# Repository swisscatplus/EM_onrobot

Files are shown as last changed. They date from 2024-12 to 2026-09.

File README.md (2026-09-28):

<br />
<div align="center">
  <a href="https://github.com/swisscatplus/EM_onrobot">
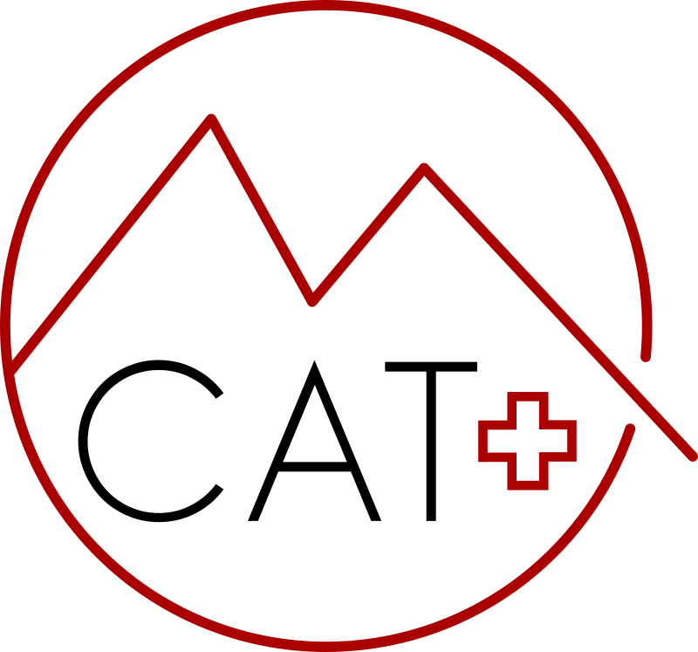
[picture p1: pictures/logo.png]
    
  </a>
  <h1 align="center">EM_onrobot</h1>
</div>

This is the software that runs **on the mobile robot** (on its Raspberry Pi). It:

- drives the two wheels from velocity commands (`cmd_vel`)
- measures how far the wheels turned (wheel odometry)
- reads the BNO055 IMU (orientation and acceleration sensor)
- finds the robot's position on the lab map with the camera and ArUco markers
- merges all of that into one position estimate (EKF, `robot_localization`)
- reports the robot's health (diagnostics)

Path planning, path following and fleet management are **not** here: they live in [EM_fleetmanager](https://github.com/swisscatplus/EM_fleetmanager), which runs on a laptop and sends commands to the robot.

> [!WARNING]
> **Protect the SD card.** The Raspberry Pi runs from an SD card, and SD cards wear out quickly when they are written to all the time. Several robots have already lost their card this way. Please:
>
> - Run `sudo ./scripts/setup_pi_sd_protection.sh` once on every new robot (see [step 6](#6-protect-the-sd-card)).
> - **Do not** record ROS bags (`ros2 bag record`), images or other large files on the robot's SD card. Record them on your laptop, or on a USB stick plugged into the robot.
> - **Do not** add `colcon build` to the container's start command, and do not change `--restart unless-stopped` in `deploy_dev.sh`. Both are set up on purpose (see [How it starts](#how-the-robot-starts-by-itself)).
> - Do not add log messages that print many times per second. If a message runs inside a loop or timer, throttle it: `self.get_logger().warn("...", throttle_duration_sec=2.0)`.
> - When you can, shut down cleanly (`sudo shutdown now`) before cutting the battery. Cutting the power while the card is being written can corrupt it.
>
> Buy "High Endurance" SD cards (for example Samsung PRO Endurance or SanDisk High Endurance) for the robots.

## Contents

1. [Words you need to know](#words-you-need-to-know)
2. [How the robot starts by itself](#how-the-robot-starts-by-itself)
3. [First-time setup of a new robot](#first-time-setup-of-a-new-robot)
4. [Everyday use](#everyday-use)
5. [Updating the code on the robot](#updating-the-code-on-the-robot)
6. [Talking to the robot from your laptop](#talking-to-the-robot-from-your-laptop)
7. [Troubleshooting](#troubleshooting)
8. [Advanced topics](#advanced-topics)

## Words you need to know

| Word | What it means here |
|---|---|
| **ROS 2** | The framework the robot software is built with. We use the **Humble** version. |
| **Node** | One small program, for example `base_controller`, which drives the wheels. The robot runs about ten nodes at the same time. |
| **Topic** | A named channel that nodes use to send each other messages, for example `/robot1/cmd_vel` (speed commands) or `/robot1/odomWheel` (wheel odometry). |
| **Namespace** | A prefix in front of every topic, such as `robot1`, so that several robots can share the same network without mixing up their topics. |
| **ROS_DOMAIN_ID** | A number that decides which machines can see each other's topics. The robot uses **10**. Your laptop must use 10 too. |
| **Launch file** | A file that starts several nodes at once. Here: `bringup.launch.py`. |
| **Docker image** | A frozen, ready-to-use copy of an operating system with ROS and all libraries installed. |
| **Docker container** | A running instance of an image. The robot software runs inside a container called `em_robot_dev`. |
| **colcon build** | The command that compiles the ROS code. It creates the `build/` and `install/` folders. |

## How the robot starts by itself

```text
Robot powers on
  └─ Raspberry Pi boots
      └─ Docker starts
          └─ Docker restarts the container "em_robot_dev" (because of --restart unless-stopped)
              └─ the container runs: ros2 launch em_robot bringup.launch.py
                  └─ all the nodes start: wheels, IMU, camera, localization, EKF, diagnostics
```

You do **not** need to start anything by hand after a power cycle, for example after charging the battery. Wait about one minute after power-on, and the robot is ready.

The code is compiled **only** when you run `./scripts/deploy_dev.sh`, never at start-up. This keeps start-up fast and saves the SD card.

## First-time setup of a new robot

Do this once per robot. Every step ends with a check: do not go to the next step until the check passes.

You need:

- the robot with its Raspberry Pi, camera, BNO055 IMU, U2D2 adapter and the two Dynamixel motors
- a charged battery (the U2D2 does **not** power the motors: the motors need the battery)
- a laptop on the same Wi-Fi network as the robot
- an internet connection for the robot during setup (to download the Docker image)

### 1. Connect to the Raspberry Pi

From your laptop, connect over SSH. Replace `<user>` and `<robot-ip>` with the robot's values (ask your supervisor):

```bash
ssh <user>@<robot-ip>
```

All the commands below run **on the robot**, in this SSH session, unless a step says otherwise.

**Check:** your terminal prompt now shows the robot's name.

### 2. Install Docker

```bash
curl -fsSL https://get.docker.com | sudo sh
sudo usermod -aG docker $USER
```

Log out (`exit`) and SSH in again so the group change applies.

**Check:** `docker run --rm hello-world` prints "Hello from Docker!".

### 3. Download this repository

```bash
cd ~
git clone https://github.com/swisscatplus/EM_onrobot.git
cd EM_onrobot
```

From now on, run every command from this `~/EM_onrobot` folder.

### 4. Give the robot its name

Every robot needs its own namespace (`robot1`, `robot2`, ...), otherwise two robots on the same network would mix their topics.

```bash
cp config/robot.local.env.example config/robot.local.env
nano config/robot.local.env
```

Set `ROBOT_NAMESPACE=robot1` (or `robot2`, ... if other robots already use `robot1`). Save with `Ctrl+O`, `Enter`, then quit with `Ctrl+X`.

This file is ignored by Git, so `git pull` never overwrites it.

**Check:** `cat config/robot.local.env` shows your namespace.

### 5. Set up the hardware access

**a. Motors: give the U2D2 a fixed name.** Linux names USB adapters `/dev/ttyUSB0`, `/dev/ttyUSB1`, ..., and the number can change at every reboot. We create a rule so the U2D2 is always called `/dev/dynamixel`.

First, plug in the U2D2 and find its IDs:

```bash
lsusb | grep -i 0403
```

You should see something like `ID 0403:6001 Future Technology Devices ...`. The part after `0403:` is the product ID (here `6001`). If yours is different, for example `6014`, use your value in `idProduct` below.

Create the rule:

```bash
sudo tee /etc/udev/rules.d/99-dynamixel.rules > /dev/null <<'EOF'
# Match the FTDI chip of the Dynamixel U2D2
SUBSYSTEM=="tty", ATTRS{idVendor}=="0403", ATTRS{idProduct}=="6001", SYMLINK+="dynamixel", MODE="0666", GROUP="dialout"
EOF
sudo udevadm control --reload-rules
sudo udevadm trigger
```

**Check:** `ls -l /dev/dynamixel` shows `/dev/dynamixel -> ttyUSB0` (the number may differ).

If another FTDI adapter is plugged into the robot, the rule can pick the wrong one. In that case, add `ATTRS{serial}=="<serial>"` to the rule, using the U2D2 serial number shown by `udevadm info -a -n /dev/ttyUSB0 | grep serial`.

**b. IMU: enable I2C.** The BNO055 is connected over I2C.

```bash
sudo raspi-config
```

Go to **Interface Options → I2C → Yes**, then reboot (`sudo reboot`).

**Check:** `ls /dev/i2c-1` exists, and `sudo i2cdetect -y 1` shows `28` in the table (the IMU's address).

**c. Camera.** **Check:** `ls /dev/video0` exists.

### 6. Protect the SD card

```bash
sudo ./scripts/setup_pi_sd_protection.sh
sudo reboot
```

This script:

- stops Linux from writing on every file read (`noatime`)
- keeps the system logs in RAM instead of on the card (they are lost at each reboot)
- turns off swap on the SD card
- limits the size of Docker logs

It backs up every file it changes (`<file>.bak.<date>`). You can run it again safely.

**Check:** after the reboot, `swapon --show` prints nothing.

### 7. Allow the robot to download the Docker image

The robot's Docker image (`ghcr.io/swisscatplus/em_onrobot/em_robot_base`) is stored on GitHub. If it is private, log in once with a GitHub account that has access. Create a token at GitHub → Settings → Developer settings → Personal access tokens, with the `read:packages` permission, then run:

```bash
docker login ghcr.io -u <your-github-username>
```

Paste the token when it asks for a password.

### 8. Deploy

Make sure the battery is connected (the motors must be powered), then:

```bash
./scripts/deploy_dev.sh
```

The first time, this downloads a large image (several GB) and can take a while. The script:

1. compiles the code once (`colcon build`)
2. stops the old container, if there is one
3. starts the `em_robot_dev` container, which launches all the nodes

**Check:** follow [Is the robot running?](#is-the-robot-running) below.

Finally, reboot the robot (`sudo reboot`) and check again: this confirms that it starts by itself.

## Everyday use

### Power on

Connect the battery and wait about one minute. Everything starts by itself.

### Is the robot running?

On the robot (over SSH):

```bash
docker ps
```

You should see `em_robot_dev` with the status `Up ...`.

- `Restarting` means that a node crashes at start-up. Read the logs, see [Troubleshooting](#troubleshooting).
- If `em_robot_dev` is missing, run `./scripts/deploy_dev.sh`.

Read the logs (`Ctrl+C` to stop reading; this does not stop the robot):

```bash
docker logs -f --tail 100 em_robot_dev
```

List the topics from inside the container:

```bash
docker exec -it em_robot_dev bash
source /opt/ros/humble/setup.bash
source /ros2_ws/install/setup.bash
ros2 topic list
```

You should see topics such as `/robot1/cmd_vel`, `/robot1/odomWheel`, `/robot1/bno055/imu` and `/robot1/odometry/filtered`. Type `exit` to leave the container.

### Useful topics

(Replace `robot1` with your robot's namespace.)

| Topic | What it contains |
|---|---|
| `/robot1/cmd_vel` | Speed commands **to** the robot (linear speed in m/s, rotation speed in rad/s) |
| `/robot1/odomWheel` | Position estimated from the wheels only |
| `/robot1/bno055/imu` | IMU data |
| `/robot1/odometry/filtered` | Best position estimate (wheels + IMU, fused by the EKF) |
| `/tf` | Positions of all the frames (`map`, `robot1/odom`, `robot1/base_link`, ...) |

See how often a topic publishes: `ros2 topic hz /robot1/odomWheel`. Print its messages: `ros2 topic echo /robot1/odomWheel`.

### Make the robot move (test)

> [!CAUTION]
> The robot will move. Put it on the floor with free space around it, or lift it so the wheels do not touch anything.

Inside the container (see above), send a slow forward command 10 times per second:

```bash
ros2 topic pub -r 10 /robot1/cmd_vel geometry_msgs/msg/Twist "{linear: {x: 0.05}, angular: {z: 0.0}}"
```

Press `Ctrl+C` to stop sending. The robot stops by itself about one second after the last command (safety watchdog).

To send the robot along a path, use [EM_fleetmanager](https://github.com/swisscatplus/EM_fleetmanager) from your laptop.

### Power off

When you can, shut down cleanly before cutting the battery:

```bash
sudo shutdown now
```

Wait until the Raspberry Pi's green LED stops blinking, then disconnect the battery.

## Updating the code on the robot

After new code was pushed to GitHub, on the robot:

```bash
cd ~/EM_onrobot
git pull
./scripts/deploy_dev.sh
```

Changed a file directly on the robot?

| What you changed | What to run |
|---|---|
| An existing Python file (`.py`) or config file (`.yaml`) | `docker restart em_robot_dev` is enough |
| Added a new file, node, message or service, or changed `setup.py` / `package.xml` | `./scripts/deploy_dev.sh` (recompiles) |
| Not sure | `./scripts/deploy_dev.sh`: it is always safe |

`docker restart` does **not** recompile. If the compilation fails, `deploy_dev.sh` stops and the robot keeps running the previous version.

## Talking to the robot from your laptop

Your laptop can see the robot's topics and send it commands, if:

1. **Both are on the same network**: the robot's Wi-Fi router.
2. **Your laptop has no other network active.** If your laptop is also plugged into another network (for example a network cable), ROS may send its discovery messages there and never find the robot. Unplug the cable, or run `nmcli dev disconnect eth0`.
3. **Your laptop uses the same domain**: `export ROS_DOMAIN_ID=10`. Put this line in your `~/.bashrc` so you do not forget it.
4. **Your laptop uses ROS 2 Humble**, like the robot. Other versions (for example Jazzy) can often list the topics, but may fail to read some messages. The simplest way to get Humble on any Linux laptop is the laptop Docker setup of EM_fleetmanager.

Then, on your laptop:

```bash
ros2 daemon stop    # forget old discovery results
ros2 topic list
```

**Check:** you see the `/robot1/...` topics.

If you do not see them:

- Check that your laptop can reach the robot: `ping <robot-ip>`.
- Check that ROS discovery can get through the network. Run `ros2 multicast receive` on your laptop, then `ros2 multicast send` on the robot, inside the container. If nothing arrives, the network or a firewall blocks discovery (`sudo ufw status`).

## Troubleshooting

First, always read the logs: `docker logs --tail 100 em_robot_dev`. Then find your error below.

| What you see | Most likely cause | What to do |
|---|---|---|
| `Failed to open Dynamixel port: /dev/dynamixel` | The U2D2 is not plugged in, or the udev rule is missing | Check `ls -l /dev/dynamixel`, and redo [step 5a](#5-set-up-the-hardware-access) |
| `Profile acceleration setup failed on motor ID=2` or `Torque enable failed on motor ID=...` | The robot can open the U2D2 but the motors do not answer. Usually the motors are not powered (battery flat or disconnected). It can also be a loose motor cable, or a motor whose ID or baud rate was changed. | Check the battery and the cables. At power-on, the LEDs on the motors should blink once. The motors must use IDs 1 (left) and 2 (right) at 57600 baud, which you can check with Dynamixel Wizard 2.0 on a laptop. |
| `Failed to read present position for motor ID=...` while running | The motor connection is lost | Check the battery level and the motor cables |
| IMU errors (`Receiving sensor data failed`, ...) | I2C is disabled or the IMU is badly connected | Redo [step 5b](#5-set-up-the-hardware-access). `sudo i2cdetect -y 1` must show `28`. |
| `docker ps` shows `Restarting` | A node crashes at start-up | Read the logs to find which one, then look for its error in this table |
| `Registry pull failed` or `unauthorized` | You are not logged in to GitHub's registry | Redo [step 7](#7-allow-the-robot-to-download-the-docker-image) |
| `lookup registry-1.docker.io ... server misbehaving` or `Temporary failure in name resolution` | The robot has no internet | Connect the robot to a network with internet access to download the image |
| The topics show on the robot but not on the laptop | Network or configuration problem | See [Talking to the robot from your laptop](#talking-to-the-robot-from-your-laptop) |
| The robot does not start after a reboot | The container was removed, or Docker does not start at boot | `sudo systemctl enable docker`, then `./scripts/deploy_dev.sh` |

Still stuck? Copy the last 100 lines of the logs (`docker logs --tail 100 em_robot_dev`) and send them to your supervisor.

## Advanced topics

The sections below are for maintainers. You do not need them to deploy and use the robot.

### Runtime profiles

A profile is a YAML file that decides which nodes start and with which settings. Profile files live in [`src/em_robot/config/profiles`](./src/em_robot/config/profiles).

| Profile | Intended system | Movement | IMU | Camera | Purpose |
|---|---|---|---|---|---|
| `real_robot` (default) | Raspberry Pi on robot | real Dynamixel base | BNO055 | Picamera2 | Production robot runtime |
| `work_ubuntu_localization_test` | Ubuntu workstation | disabled | disabled | OpenCV camera | Desktop validation of marker localization |

`deploy_dev.sh` uses `real_robot` unless you set `EM_ROBOT_PROFILE_VALUE` in `config/robot.local.env`. The container runs:

```bash
ros2 launch em_robot bringup.launch.py profile:=real_robot namespace:=robot1
```

The runtime URDF used by `robot_state_publisher` is packaged with `em_robot` at [`src/em_robot/urdf/simple_box_robot.urdf`](./src/em_robot/urdf/simple_box_robot.urdf). Hardware design files are intentionally kept outside this software repository.

### What `deploy_dev.sh` does

1. Loads `config/robot.local.env` (namespace, profile).
2. Picks the base image: the local `em_robot_base:local` if it exists, otherwise it pulls `ghcr.io/swisscatplus/em_onrobot/em_robot_base:latest`. `ALLOW_LOCAL_BASE_BUILD=1` builds it on the robot if the pull fails (this takes a very long time on a Raspberry Pi).
3. Runs `colcon build --symlink-install` once, in a throwaway container. The workspace is bind-mounted, so `build/` and `install/` are written to the repository folder. colcon's own logs are discarded.
4. Replaces the `em_robot_dev` container. That container only runs `ros2 launch`, with:
   - `--restart unless-stopped`, which restarts it at boot. Do not use `on-failure`: Docker does not restart those containers at boot.
   - Docker logs capped at 2 × 10 MB
   - `/root/.ros/log` and `/tmp` in RAM (tmpfs)
   - host networking, so ROS discovery works on the robot's network
   - access to `/dev` (motors, camera, I2C)

### Ubuntu validation

Use this when validating localization with a USB camera on an Ubuntu workstation:

```bash
export EM_ROBOT_CAMERA_DEVICE=/dev/video0
./scripts/start_dev.sh work_ubuntu_localization_test
```

Stop it with:

```bash
./scripts/start_dev.sh work_ubuntu_localization_test down
```

The validation profile uses:

- calibration from [`src/em_robot/config/calibration_ubuntu_test.yaml`](./src/em_robot/config/calibration_ubuntu_test.yaml)
- marker map from [`src/em_robot/config/marker_map_laptop_test.yaml`](./src/em_robot/config/marker_map_laptop_test.yaml)
- RViz layout from [`src/em_robot/rviz/localization_debug.rviz`](./src/em_robot/rviz/localization_debug.rviz)

### Marker survey

Run marker survey on the robot:

```bash
./scripts/run_marker_survey.sh real_robot single-shot
```

Run marker survey from the Ubuntu validation container:

```bash
export EM_ROBOT_CAMERA_DEVICE=/dev/video0
./scripts/run_marker_survey.sh work_ubuntu_localization_test single-shot
```

Manual mode keeps the node alive and lets you set the known robot pose before saving visible markers:

```bash
./scripts/run_marker_survey.sh real_robot manual 0.0 0.0 0.0
```

### Camera calibration

Set up the local calibration environment:

```bash
./scripts/setup_calibration_env.sh
```

Capture images:

```bash
./scripts/capture_calibration_images.sh
```

Compute calibration:

```bash
./scripts/run_camera_calibration.sh
```

Validate ArUco distance:

```bash
./scripts/validate_aruco_distance.sh
```

Generated calibration images, validation outputs, and recorded bags are ignored by Git. Calibration images are written to disk: on the robot, keep their number small (see the SD card warning at the top).

### Build and test

Build the ROS workspace (inside a ROS 2 Humble environment):

```bash
colcon build --symlink-install --packages-select em_robot em_robot_srv bno055
```

Run tests:

```bash
colcon test --packages-select em_robot em_robot_srv bno055
colcon test-result --verbose
```

For a quick source-only unit smoke test outside a fully built ROS workspace:

```bash
PYTHONPATH=src/em_robot python3 -m pytest src/em_robot/test -q \
  --ignore=src/em_robot/test/test_copyright.py \
  --ignore=src/em_robot/test/test_flake8.py \
  --ignore=src/em_robot/test/test_pep257.py
```

Run the tests on your laptop rather than on the robot, to spare the SD card.

### Repository layout

```text
EM_onrobot/
├── config/
│   ├── fastdds.xml                 # ROS network (DDS) settings
│   └── robot.local.env.example     # per-robot settings template (copy to robot.local.env)
├── docker/
│   ├── compose.yaml                # Ubuntu validation workflow
│   ├── compose.ubuntu.yaml
│   ├── Dockerfile
│   ├── Dockerfile.base             # robot base image (ROS Humble + libcamera + Dynamixel SDK)
│   ├── Dockerfile.desktop
│   └── entrypoint.sh
├── scripts/
│   ├── deploy_dev.sh               # build + (re)start the robot container
│   ├── setup_pi_sd_protection.sh   # one-time SD card protection for a new robot
│   └── ...                         # calibration, marker survey, image builds
├── src/
│   ├── em_robot/                   # main package: nodes, launch file, config, profiles
│   ├── em_robot_srv/               # custom ROS services
│   └── bno055/                     # IMU driver (vendored)
└── pictures/
```

### Dependency notes

`em_robot` is an `ament_python` package. ROS/system dependencies are declared in `package.xml` where rosdep keys exist. Picamera2 and libcamera are provided by the robot Docker base image because the Raspberry Pi camera stack is built there rather than resolved by rosdep.

The vendored `bno055` package keeps its upstream BSD license in [`src/bno055/LICENSE`](./src/bno055/LICENSE).

## License

MIT. See [`LICENSE`](./LICENSE).

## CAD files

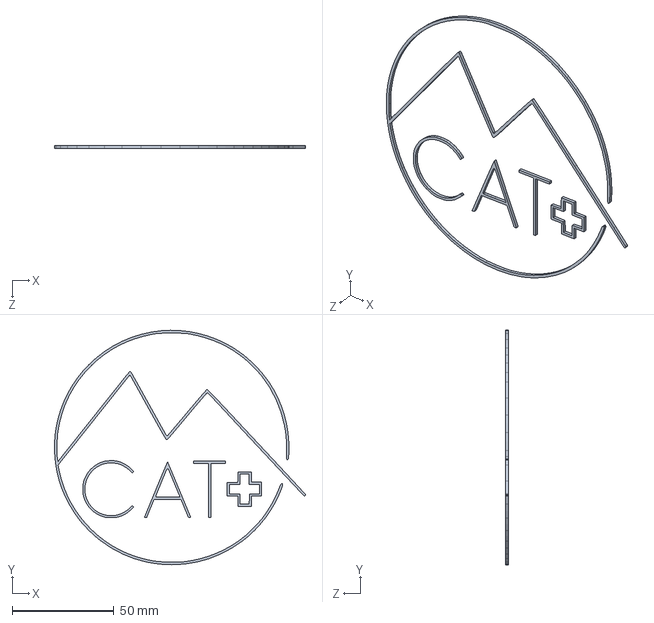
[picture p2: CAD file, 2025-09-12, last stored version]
CAD/EdyMobileURDFAssembly/Logo3^EM assembly.SLDPRT
123.1 x 115.0 x 1.30 mm

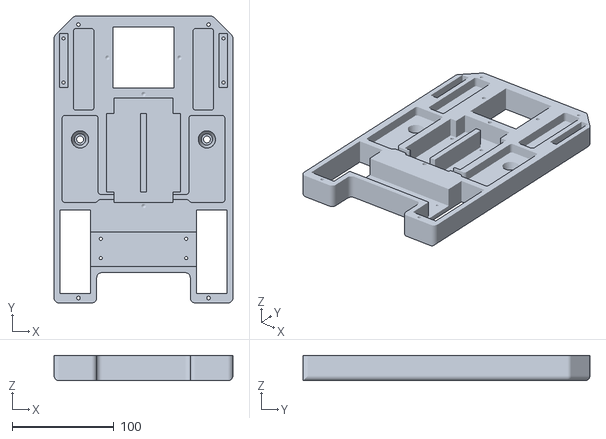
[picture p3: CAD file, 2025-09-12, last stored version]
CAD/Edymobile_STL_And_BambuPrintables/Edymobile/Chassis.STL
176.0 x 282.3 x 25.0

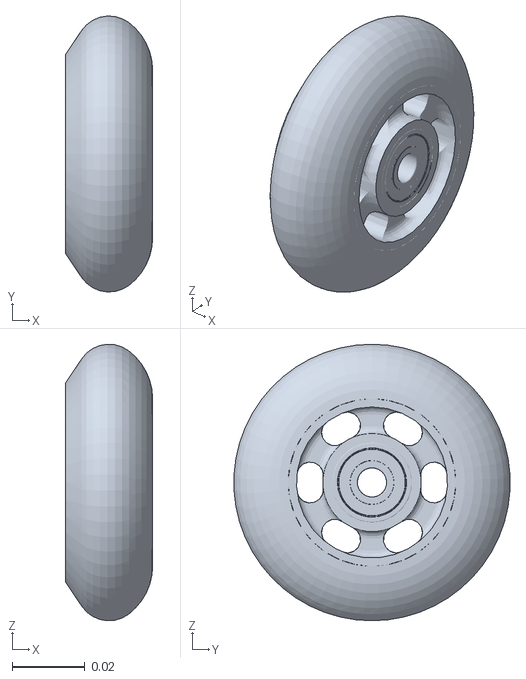
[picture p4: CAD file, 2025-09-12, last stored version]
CAD/EdyMobile_URDF_screencast_ROS/URDF_screencast_ROS/meshes/wheel_right_link.STL
0.024 x 0.0758 x 0.076

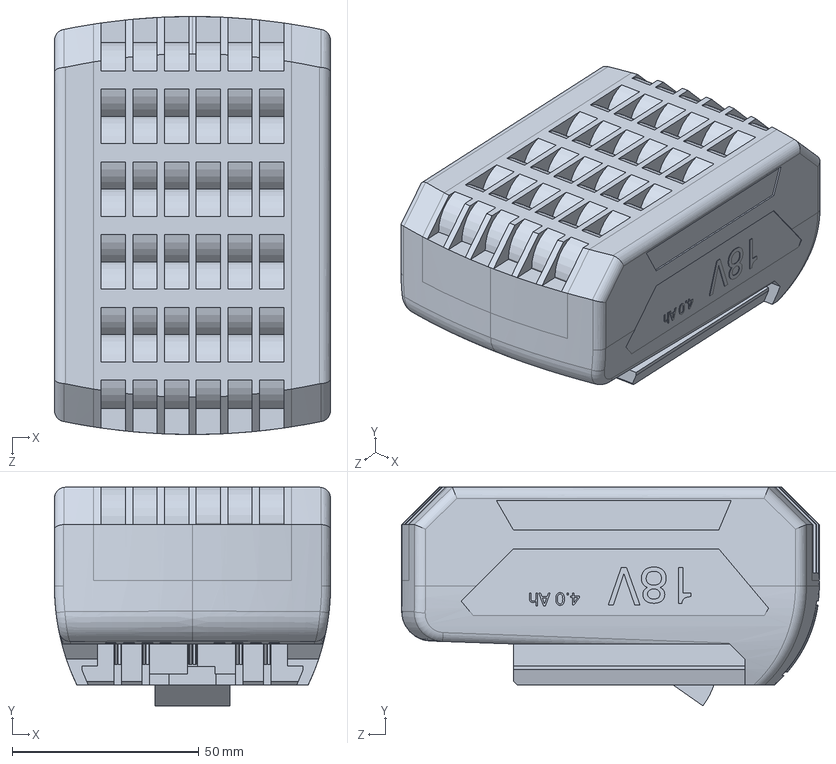
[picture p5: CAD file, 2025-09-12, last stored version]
CAD/EdyMobileAssembly/Battery Li-ion 18V, 4Ah.step.SLDPRT
74.0 x 58.6 x 112.0 mm

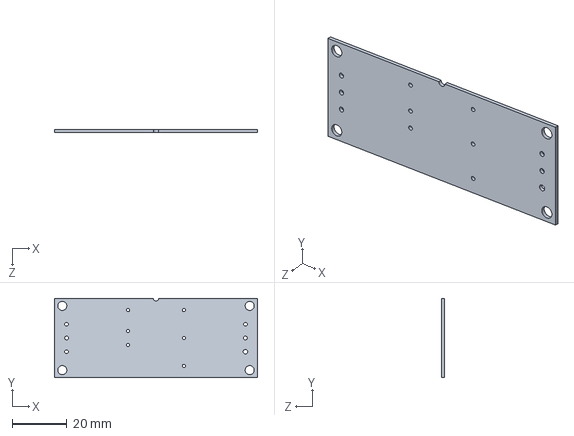
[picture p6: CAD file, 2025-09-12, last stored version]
CAD/EdyMobileURDFAssembly/dtj1524s05_01.SLDPRT
73.9 x 28.9 x 1.00 mm

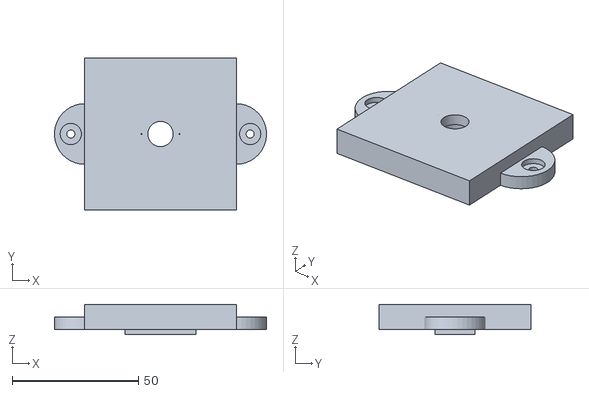
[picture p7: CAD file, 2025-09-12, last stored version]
CAD/Edymobile_STL_And_BambuPrintables/Edymobile/Roomba wheel module.STL
83.9 x 60.0 x 12.0

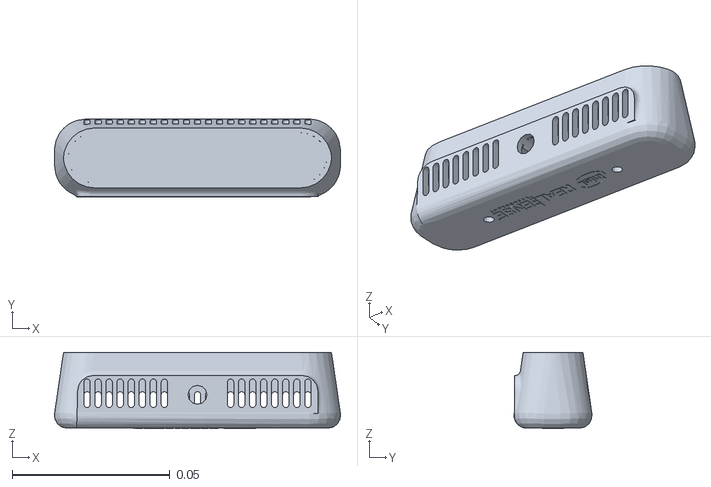
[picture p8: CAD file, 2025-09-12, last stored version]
CAD/EdyMobile_URDF_screencast_ROS/URDF_screencast_ROS/meshes/depth_camera_link.STL
0.0907 x 0.0247 x 0.0241

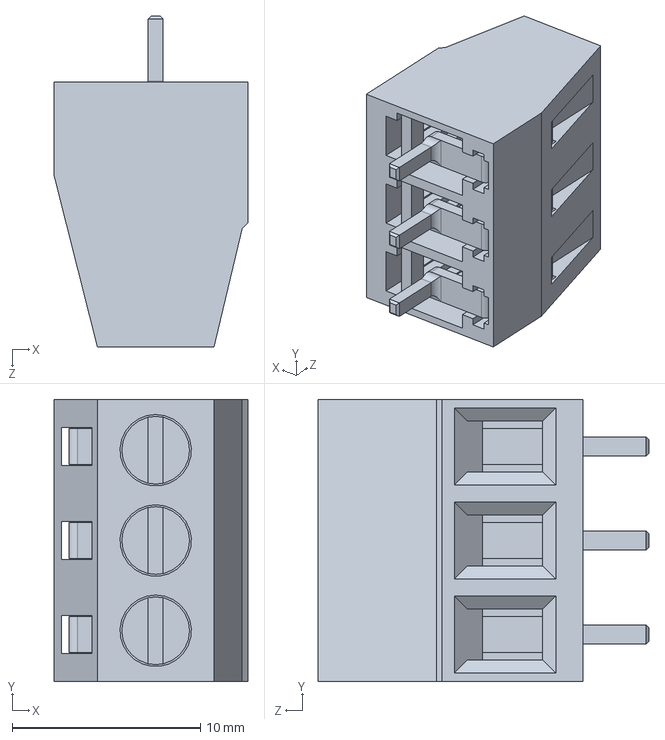
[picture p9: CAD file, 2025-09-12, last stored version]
CAD/EdyMobileAssembly/dtj1524s05_04.SLDPRT
10.3 x 15.0 x 17.6 mm

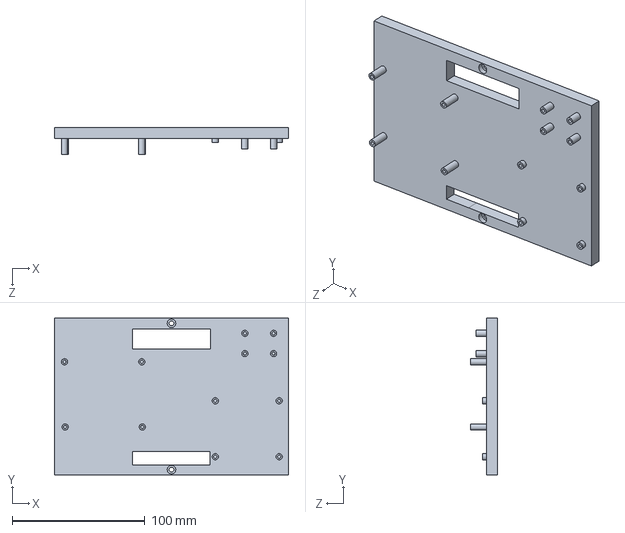
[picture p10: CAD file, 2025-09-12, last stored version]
CAD/EdyMobileURDFAssembly/Components plateforme.SLDPRT
176.0 x 118.0 x 20.0 mm

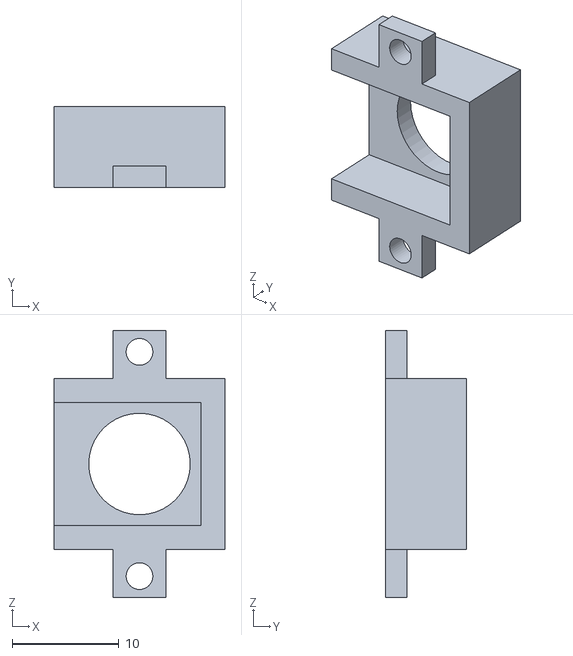
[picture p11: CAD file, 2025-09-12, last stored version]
CAD/Edymobile_STL_And_BambuPrintables/Edymobile/Camera blocker.STL
16.0 x 7.60 x 25.0

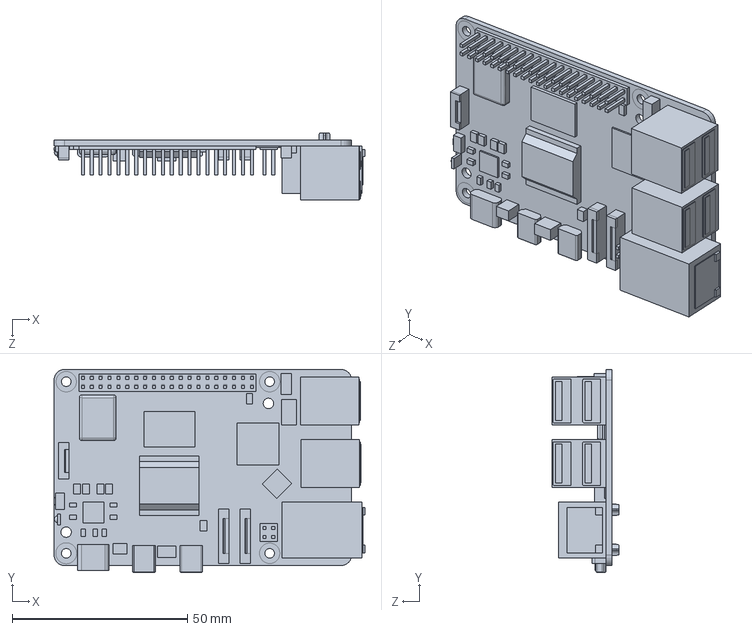
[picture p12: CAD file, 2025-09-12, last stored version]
CAD/EdyMobileAssembly/Raspberry Pi 5.SLDPRT
88.8 x 58.0 x 19.2 mm

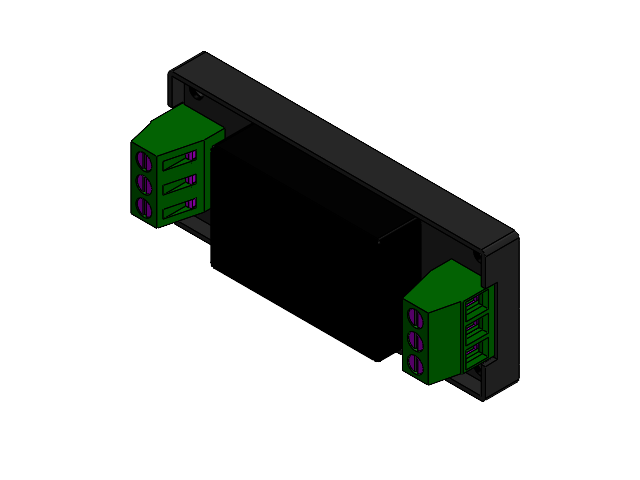
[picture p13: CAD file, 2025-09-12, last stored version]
CAD/EdyMobileAssembly/dtj1524s05.SLDASM
dtj1524s05_01
dtj1524s05_02
dtj1524s05_03
dtj1524s05_04
dtj1524s05_05

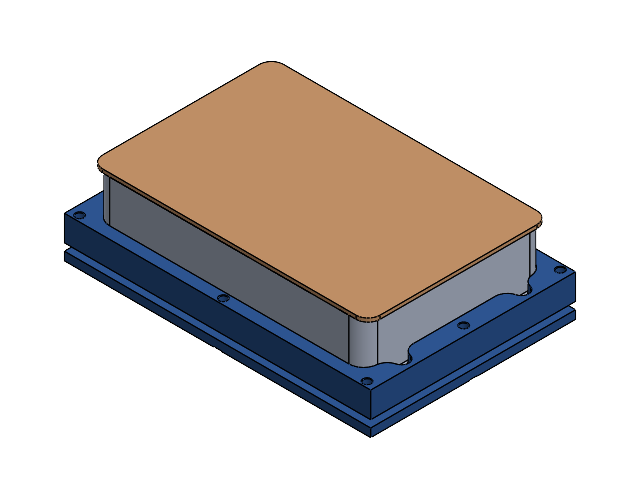
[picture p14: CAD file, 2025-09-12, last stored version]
CAD/EdyMobileAssembly/ASSEMBLAGE_COMPLET_VMAGNET.SLDASM
Y_MID_INTERFACE_3_VMAGNET
BOTTOM_VMAGNET
JOINT_PLAT
VIALE_D6 x 96

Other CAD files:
CAD/EdyMobileURDFAssembly/dtj1524s05.SLDASM
CAD/EdyMobileURDFAssembly/base_link.SLDASM
CAD/EdyMobileAssembly/Logo3^EM assembly.SLDPRT
CAD/EdyMobileURDFAssembly/ASSEMBLAGE_COMPLET_VMAGNET.SLDASM
CAD/EdyMobile_URDF_screencast_ROS/URDF_screencast_ROS/meshes/wheel_left_link.STL
CAD/EdyMobileAssembly/Adafruit neopixel ring.SLDPRT
CAD/EdyMobileAssembly/Adafruit neopixel ring.stp
CAD/EdyMobileAssembly/Adafruit_BNO055_IMU.SLDPRT
CAD/EdyMobileAssembly/BOTTOM_VMAGNET.SLDPRT
CAD/EdyMobileAssembly/Battery module.SLDPRT
CAD/EdyMobileAssembly/Battery wires module.SLDPRT
CAD/EdyMobileAssembly/Bridge.SLDPRT
CAD/EdyMobileAssembly/Camera and LED module.SLDPRT
CAD/EdyMobileAssembly/Camera blocker.SLDPRT
CAD/EdyMobileAssembly/Chassis.SLDPRT
CAD/EdyMobileAssembly/Heat Set Insert - M2 5mm x 4mm (ODxL) v3.SLDPRT
CAD/EdyMobileAssembly/Heat Set Insert - M2 5mm x 4mm (ODxL) v3.step
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

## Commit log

2024-06-27 debugging cam frame size
2024-06-27 fixing log for cam frame
2024-07-04 changed imu topic frame
2024-07-12 Implemented config yaml file for camera node at launch level
2024-07-12 getting rid of calibration
2025-02-18 test to add camera in dockerfile
2025-02-19 remove build of base
    base is built directly on the raspberry pi because it crashes otherwise
2025-02-26 add 90 degree offset because camera is offset
2025-02-27 add calibration python files
2025-02-27 remove optical sensor
2025-03-05 change ekf to match new topic from camera
2025-04-08 add camera to odom
2025-04-15 change frame for odom ?
2025-04-29 remove temporarly camera
2025-09-10 Change ReadMe and add Schematics
    [Em_robot_Electrical_Schematics.kicad_pcb, Em_robot_Electrical_Schematics.kicad_sch]
2025-09-10 Add Electrical Schematics
    [Em_robot_Electrical_Schematics.kicad_sch]
2025-09-12 ADD CAD
    [ASSEMBLAGE_COMPLET_VMAGNET.SLDASM, Adafruit neopixel ring.SLDPRT, Adafruit neopixel ring.stp, Adafruit_BNO055_IMU.SLDPRT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]
2025-10-08 try to solve usb device not seen by docker
2026-04-21 Clean up code and fix critical deployment issues
    - Fix BNO055 config path in launch file (was looking in wrong directory)
    - Remove disabled em_odom.py node and references
    - Remove duplicate aruco_detection.py submodule
    - Remove unused imports (TransformStamped, euler_from_quaternion, numpy, BuiltinTime)
    - Remove unused PoseStamped publisher from em_localization
    - Add camera_height and marker_size to calibration.yaml
    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
2026-04-21 correct camera ccepting first tag
2026-04-22 Add desktop_replay, diagnostics, and marker map
    Introduce a new desktop_replay profile and supporting infrastructure for replay-based localization and runtime diagnostics. Key additions:
    - New profile: src/em_robot/config/profiles/desktop_replay.yaml and docs updates (README.md, DEVELOPMENT_WORKFLOWS.md) with keyboard teleop and replay instructions. Added data/replays/.gitkeep as pla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
    - Camera/IO: OpenCV source now supports looping replays (camera_sources), and localization node accepts camera_loop and reports capture errors.
    - Localization: marker_map.yaml, marker_map loader and static publisher (marker_map_loader.py, marker_map_publisher.py) to publish marker TFs and diagnostics.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
2026-04-23 Add wall detection with motor load, to test
2026-04-24 add led support
2026-04-24 prepare calib camera
2026-04-24 calibration ready
2026-04-24 add calibration control
2026-04-24 add camera in rviz2
2026-04-24 add camera vizu
2026-04-28 add camera debug
2026-04-28 add markers calibration
2026-04-28 cortrect joint state publisher
2026-04-28 remove led and correct typo
2026-04-28 test a better smoothing of camera, this one it pulls the robot instead of TP
2026-04-28 Revert "test a better smoothing of camera, this one it pulls the robot instead of TP"
    This reverts commit 405fdd66d0f24e5e3a6315d43e2331174f87df8a.
2026-04-28 Revert "Update calibration.yaml"
    This reverts commit bb76997ed2f4f277d63befd6a5625bb28f3083a5.
2026-04-28 Reapply "Update calibration.yaml"
    This reverts commit 25bb6c938a7c04c52357f91e07d75a3ff595bab4.
2026-04-28 Reapply "test a better smoothing of camera, this one it pulls the robot instead of TP"
    This reverts commit 8319a54ba20d5d8050fea532c746605c6ac54954.
2026-04-29 try a second round of improving loca with camera with timestamp
2026-04-30 refractor for main
    [ASSEMBLAGE_COMPLET_VMAGNET.SLDASM, Adafruit neopixel ring.SLDPRT, Adafruit neopixel ring.stp, Adafruit_BNO055_IMU.SLDPRT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]
